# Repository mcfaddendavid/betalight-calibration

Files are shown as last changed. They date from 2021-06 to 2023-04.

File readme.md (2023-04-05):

# GTLS-based calibration source for cameras

-- David McFadden

This page describes a mount for a Gaseous Tritium Light Source (GTLS or
"betalight"). The mount is designed to illuminate the image plane of a c-mount
camera and produce a spot size of approximately 4mm.

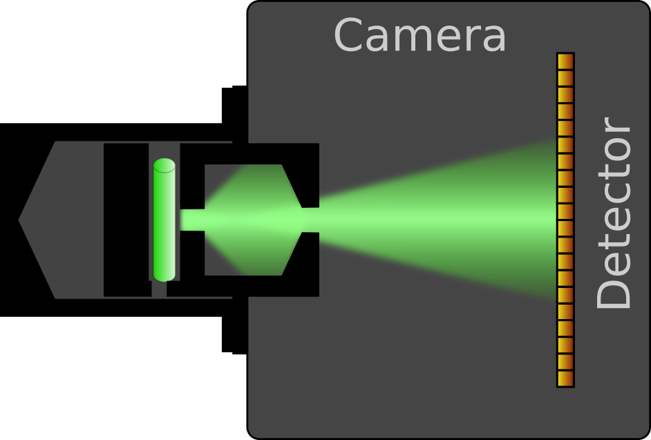
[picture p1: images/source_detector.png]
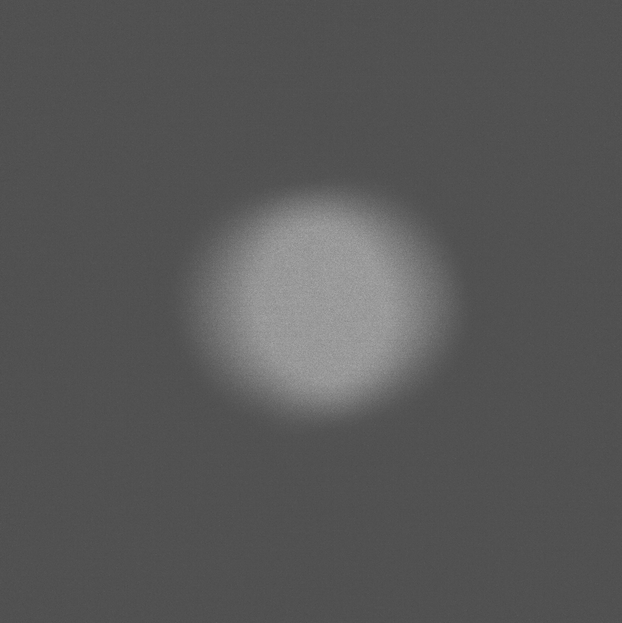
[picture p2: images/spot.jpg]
 

### Non-printed parts

| Number | Description                                                         | Possible supplier                                                                                                                                           | Approx. Price |
| ------ | ------------------------------------------------------------------- | ----------------------------------------------------------------------------------------------------------------------------------------------------------- | ------------- |
| 1      | Thorlabs C-mount retaining ring                                     | https://www.thorlabs.de/thorproduct.cfm?partnumber=CMRR                                                                                                     | 11.52 EUR     |
| 1      | Thorlabs CS- to C-Mount Extension Adapter                           | https://www.thorlabs.de/thorproduct.cfm?partnumber=CML05                                                                                                    | 16.78 EUR     |
| 1      | Cylindrical GTLS light source 2 mm x 12 mm (green colour suggested) | - http://www.beta-master.com/ (EU) <br> - https://www.total-fishing-tackle.com/gardner-tritium-max-betalights-isotopes (UK)  <br> - https://www.mixglo.com/ (International shipping) <br> - various sellers on eBay etc. | 8.80 EUR      |

Betalights are available from various suppliers in different countries. They are
also used as fishing tackle, and are stocked by various sellers of fishing
equipment. They can also easily be found on sites like eBay or Amazon, where
various smaller vendors offer them. Search terms include "betalight", "tritium
vial" and "GTLS".

The amount of radioactive tritium is very small and exempt from regulation in
Germany and many other countries. Nevertheless, local regulations will depend on
your country.

### 3D printed parts

| Number | Description               | Comments                                            |
| ------ | ------------------------- | --------------------------------------------------- |
| 1      | Core                      | Print with support, support threshold at 72 degrees |
| 1      | Top hat                   | No support necessary                                |
| 1      | Extraction tool           | No support necessary                                |
| 1      | Centering cool (optional) | No support necessary                                |

## Printing and assembly

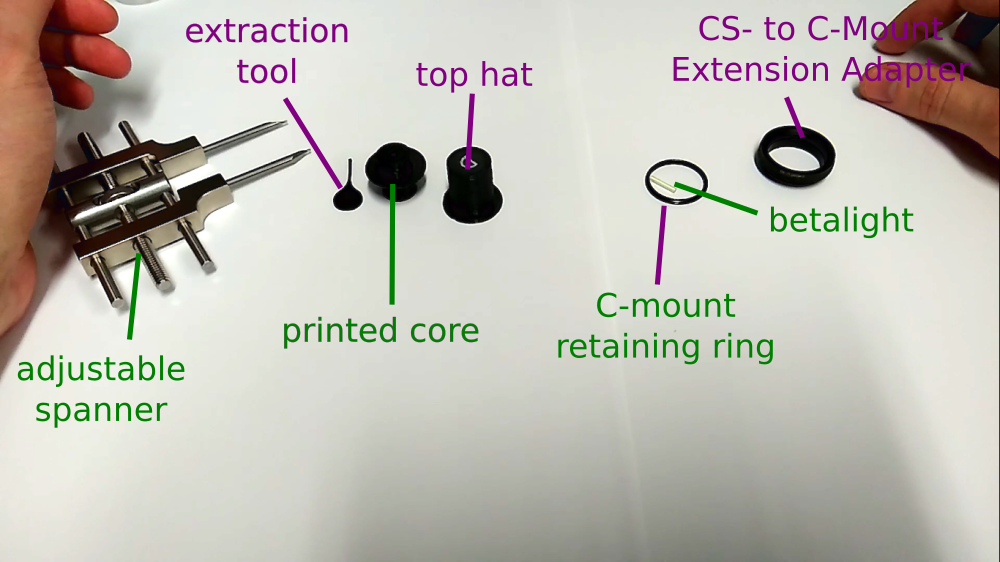
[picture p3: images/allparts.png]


The parts have all been printed and tested on FDM printers, in particular the
Ultimaker 3. The core and "top hat" parts should be printed in a black material. 

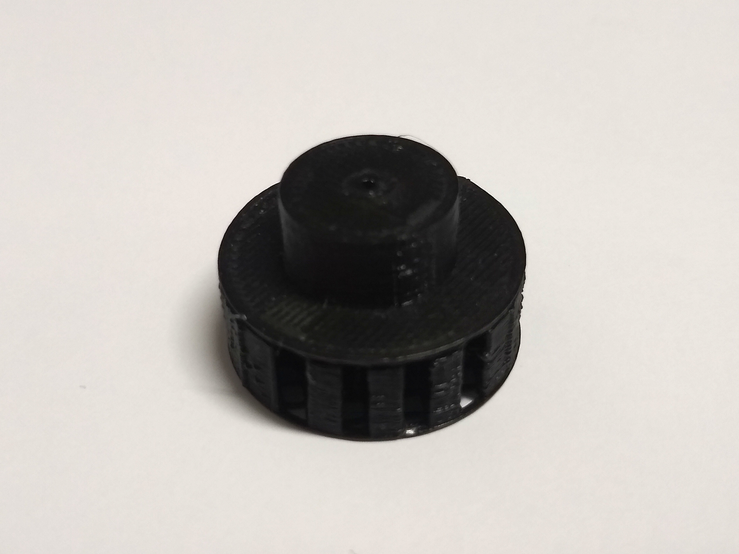
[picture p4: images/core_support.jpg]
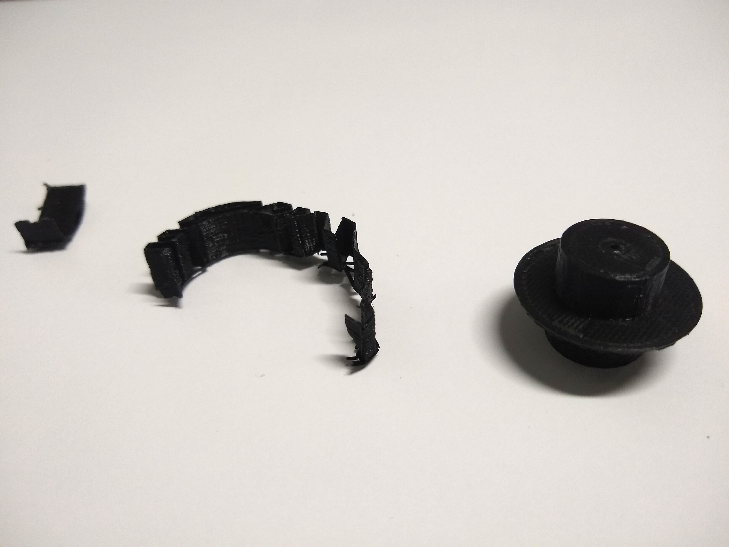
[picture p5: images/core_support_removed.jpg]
 

The core part needs to be printed with support, but it is also important that no
support is generated within the cavity behind the exit aperture. Setting the
"support overhang angle" (Cura) or equivalent setting in your slicer program to
72 degrees should ensure that this does not happen.

The core has a slot that is supposed to *lightly* grip the cylindrical GTLS
so that it stays in place, but also needs to be easy to insert and remove using the
extraction tool. Because of this, the tolerances are relatively low, and you
will probably need to fine-tune the horizontal expansion (Cura) or equivalent
setting.

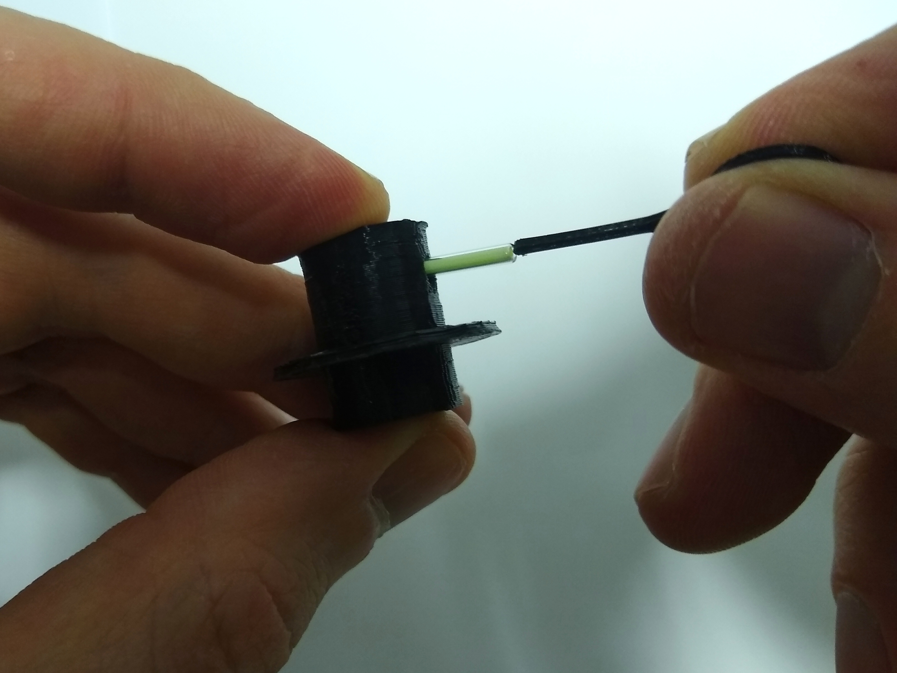
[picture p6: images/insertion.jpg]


https://user-images.githubusercontent.com/25613833/123168351-25300480-d478-11eb-8fc2-01346910f70a.mp4

**Do not use excessive force on the glass tubes**, as they may break. Use the
printed "exctraction tool" to push the tube into the slot. If you can't push it into
the slot using the extraction tool, it is probably better to reprint the core
with a slightly bigger hole.

Alternatively, the subfolder "core_different_tolerances" contains STL files with
a range of different slot sizes. If you find that the slot is either too tight
or too loose, you can print a different file without changing the print
settings. The standard file is "2.290mm.stl".

I will probably tweak the tolerances further, so please back up any STL files
you successfully print. Openscad design files will follow soon.

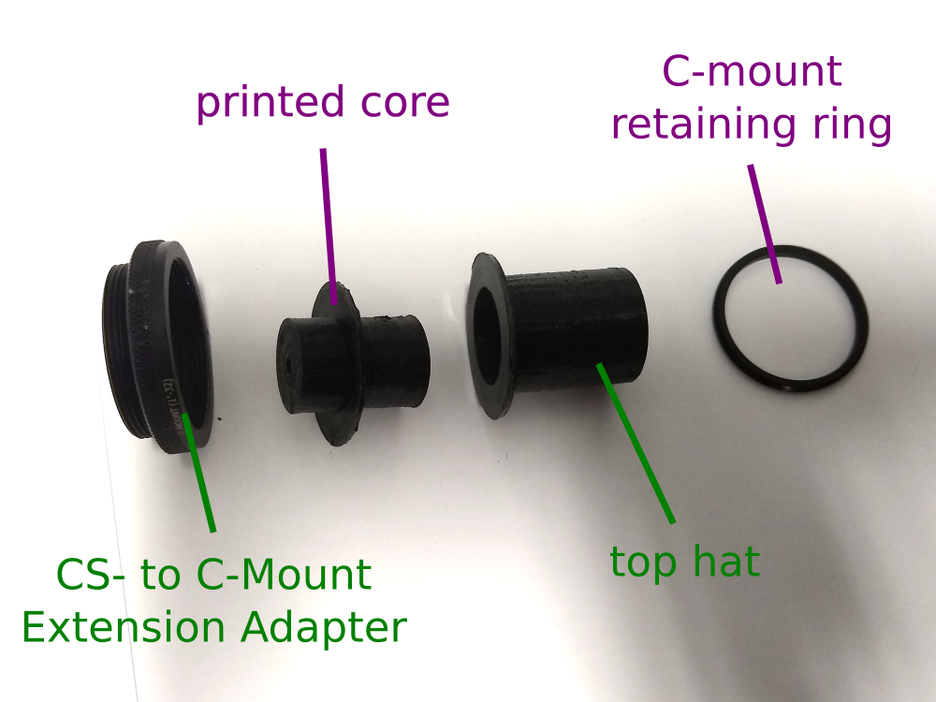
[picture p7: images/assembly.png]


In order to block ambient light, a cover (shaped like a top hat) is attached.
The two parts are then fixed into the Thorlabs extension adapter using the
retaining ring.

An adjustable spanner or other suitable tool needs to be used to tighten the
ring. You may need to reverse the blades to get enough clearance from the
plastic.

Before tightening the ring, the core might have a small amount of play in the XY
direction. You might therefore want to centre the part with the optional
centring tool before tightening. This may be useful for detectors with a small
area. Note that the tolerances are also relatively small for this part and you
will likely need to adjust the horizontal expansion settings.

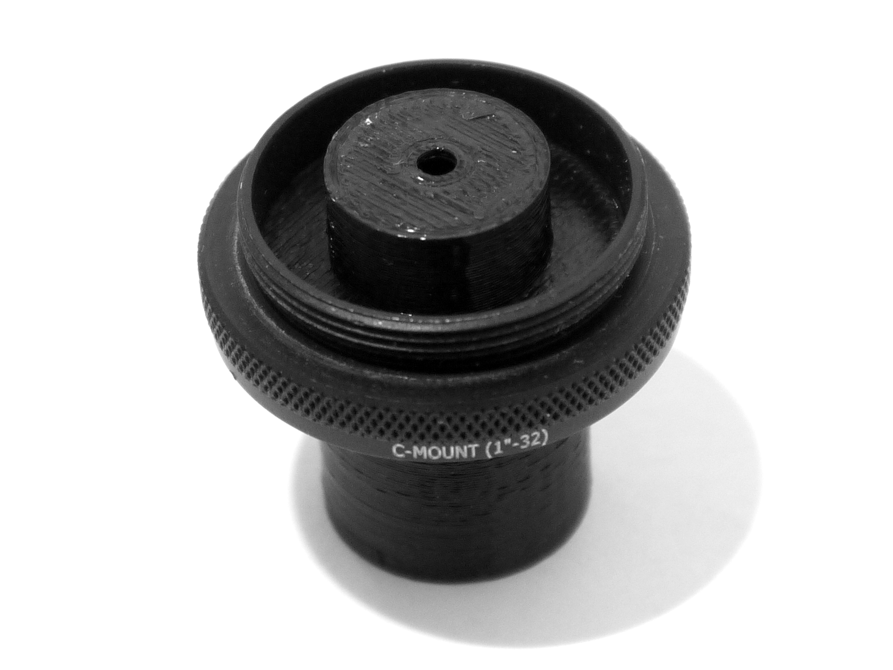
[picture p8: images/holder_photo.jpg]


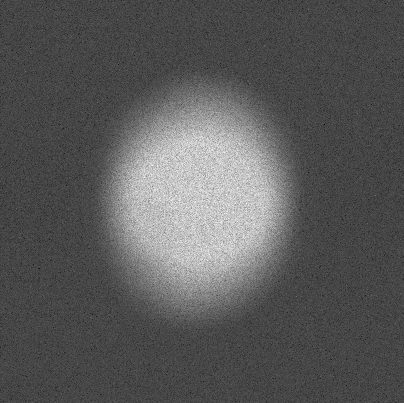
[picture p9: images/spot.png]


## Analysis

The calibration can be performed using the photon transfer method. This can easily
be done with the [NanoImagingPack library](https://gitlab.com/bionanoimaging/nanoimagingpack/-/tree/feature2-calreadnoise). (Scroll down for installation instructions. Requires python and numpy)

For convenience we also wrote a GUI wrapper for the calibration routine
specifically. For people who are unable to install python, we made a standalone build for Windows machines (x64) which can be downloaded from the [releases page](https://github.com/mcfaddendavid/betalight-calibration/releases) (download and extract the zip file "gui-calibration-tool-vxxx.zip". The .exe file should run on Windows 7 and later.)
Beware that this tool is in an experimental state and liable to change.

https://user-images.githubusercontent.com/25613833/123278240-12184580-d507-11eb-8506-f74449989370.mp4

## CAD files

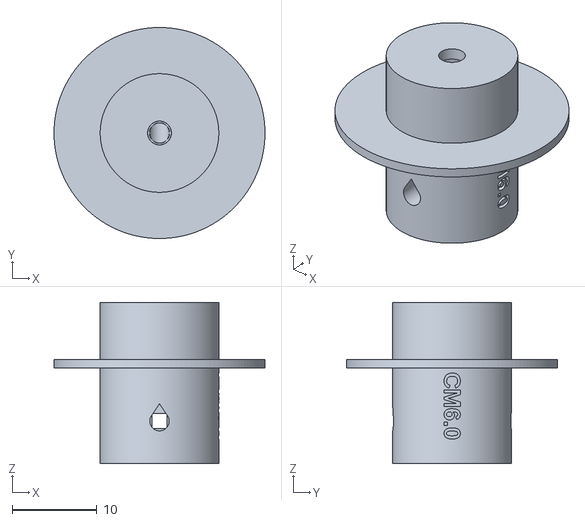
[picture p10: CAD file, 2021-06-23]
3D_files/STL_files/core.stl
24.9 x 24.9 x 19.0

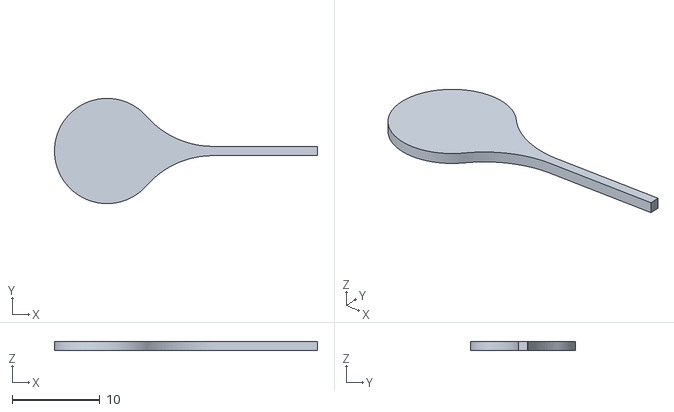
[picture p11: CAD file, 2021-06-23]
3D_files/STL_files/extraction_tool.stl
30.0 x 12.0 x 1.07

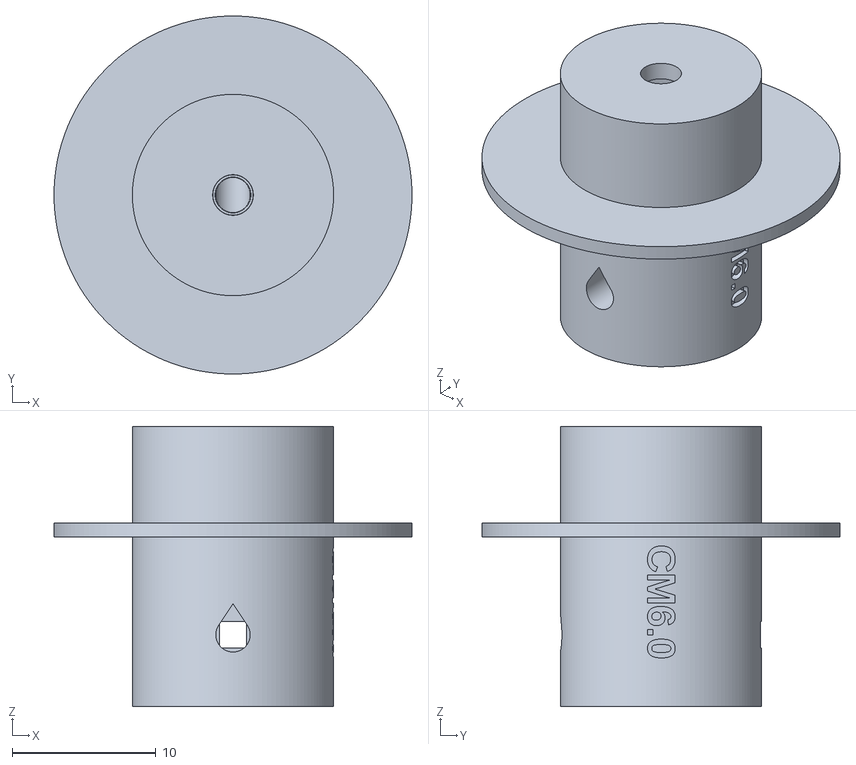
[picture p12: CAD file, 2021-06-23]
3D_files/STL_files/core_(various_tube_diameters)/2.390mm.stl
24.9 x 24.9 x 19.5

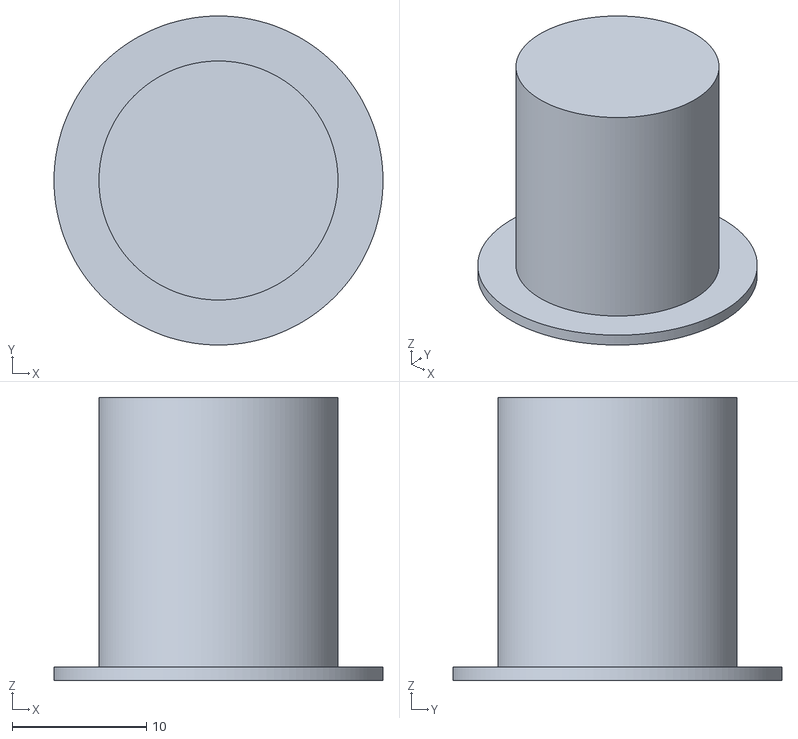
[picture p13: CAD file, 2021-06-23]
3D_files/STL_files/top_hat.stl
24.5 x 24.5 x 21.1

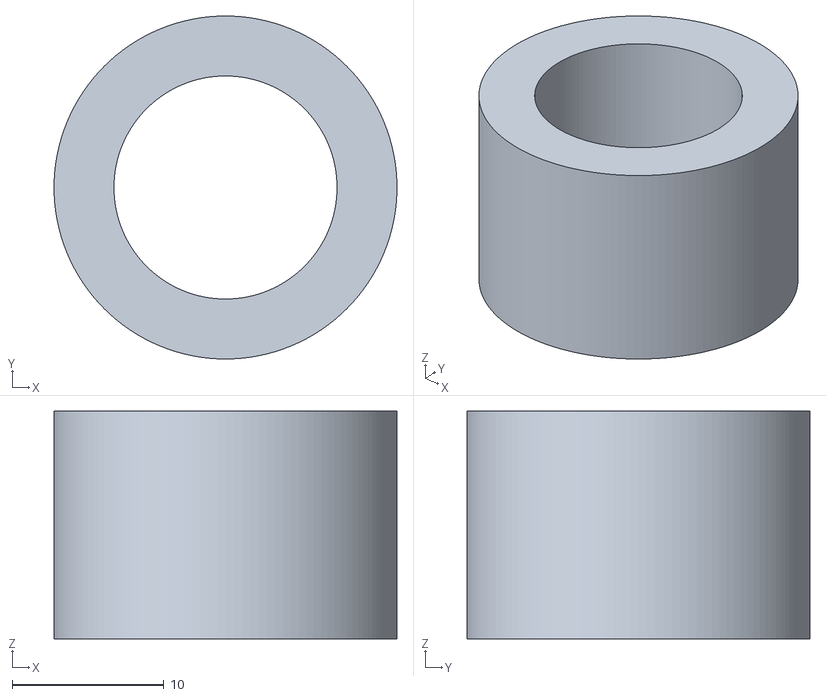
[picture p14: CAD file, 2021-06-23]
3D_files/STL_files/centering_tool.stl
22.6 x 22.6 x 15.0

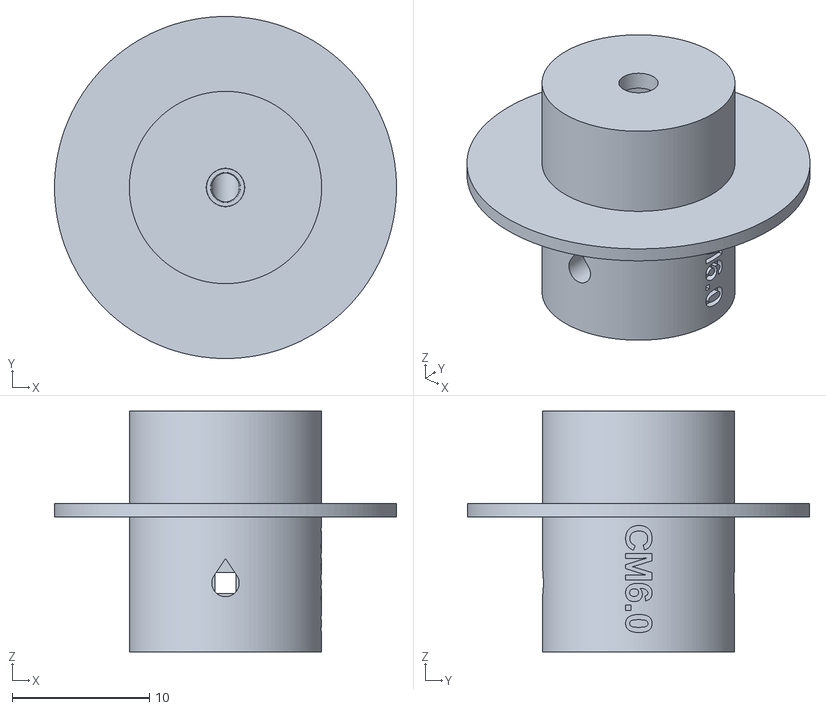
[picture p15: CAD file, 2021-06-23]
3D_files/STL_files/core_(various_tube_diameters)/1.990mm.stl
24.9 x 24.9 x 17.5

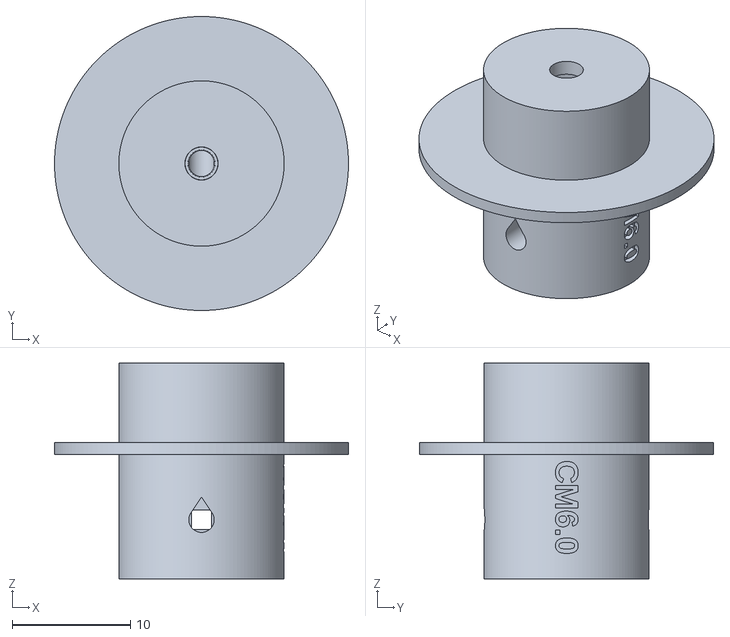
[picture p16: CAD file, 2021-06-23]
3D_files/STL_files/core_(various_tube_diameters)/2.140mm.stl
24.9 x 24.9 x 18.3

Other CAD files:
3D_files/STL_files/core_(various_tube_diameters)/2.240mm.stl
3D_files/STL_files/core_(various_tube_diameters)/2.190mm.stl
3D_files/STL_files/core_(various_tube_diameters)/2.490mm.stl
3D_files/STL_files/core_(various_tube_diameters)/2.415mm.stl
3D_files/STL_files/core_(various_tube_diameters)/2.515mm.stl
3D_files/STL_files/core_(various_tube_diameters)/2.090mm.stl
3D_files/STL_files/core_(various_tube_diameters)/2.265mm.stl
3D_files/STL_files/core_(various_tube_diameters)/2.065mm.stl
3D_files/STL_files/core_(various_tube_diameters)/2.465mm.stl
3D_files/STL_files/core_(various_tube_diameters)/2.540mm.stl
3D_files/STL_files/core_(various_tube_diameters)/2.215mm.stl
3D_files/STL_files/core_(various_tube_diameters)/2.015mm.stl
3D_files/STL_files/core_(various_tube_diameters)/2.040mm.stl
3D_files/STL_files/core_(various_tube_diameters)/2.115mm.stl
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

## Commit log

2021-06-23 Add 3D files
    [1.990mm.stl, 2.015mm.stl, 2.040mm.stl, 2.065mm.stl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]
2022-02-21 Add calibration image to readme
